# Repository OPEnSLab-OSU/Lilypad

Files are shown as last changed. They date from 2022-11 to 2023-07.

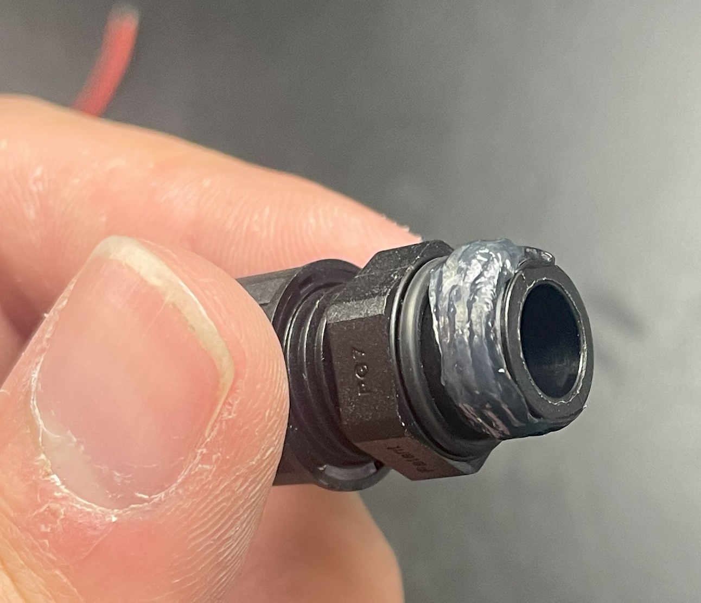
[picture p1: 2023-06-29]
Documentation/images/ElectronicsBoxAssembly/IMG_1301.jpg

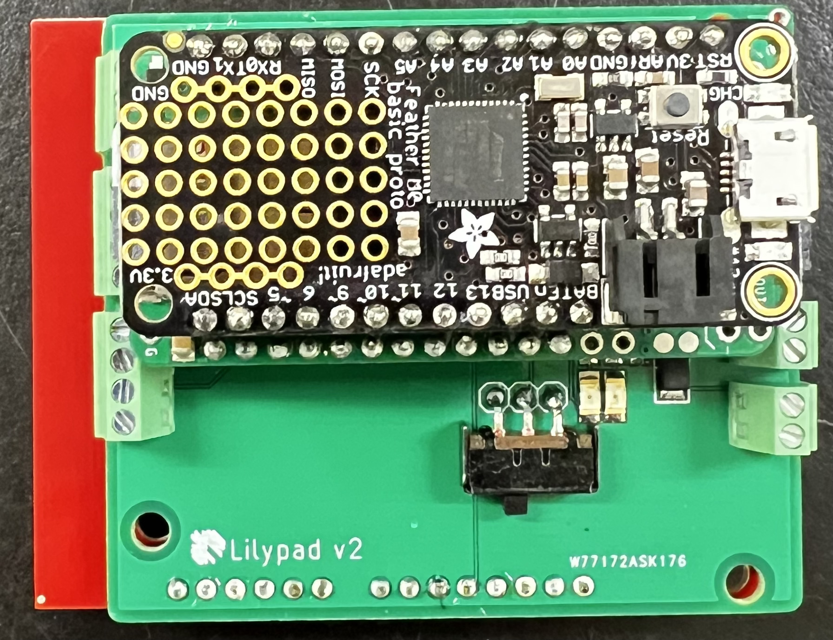
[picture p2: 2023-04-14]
Documentation/images/Hardware/stackup.jpg

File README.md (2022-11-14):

# Lilypad | [Wiki](https://github.com/OPEnSLab-OSU/Lilypad/wiki)
Project Lead: **Colin Hale-Brown**
Project Members: **Cameron Whitlow**, **Aiden Olsen**

Interested in the project? Email us at: halebroc@oregonstate.edu

The Lilypad is a floating water monitoring solution. It is able to measure water temperature, air temperature, humidity, and solar energy per square meter. It is designed to be easy to transport and deployed for at least 1 year at a time.

More information about assembly, testing, and operation can be found at the [wiki](https://github.com/OPEnSLab-OSU/Lilypad/wiki).

Ensure the 4G board has its switched in the Hardware and Shield orientations.

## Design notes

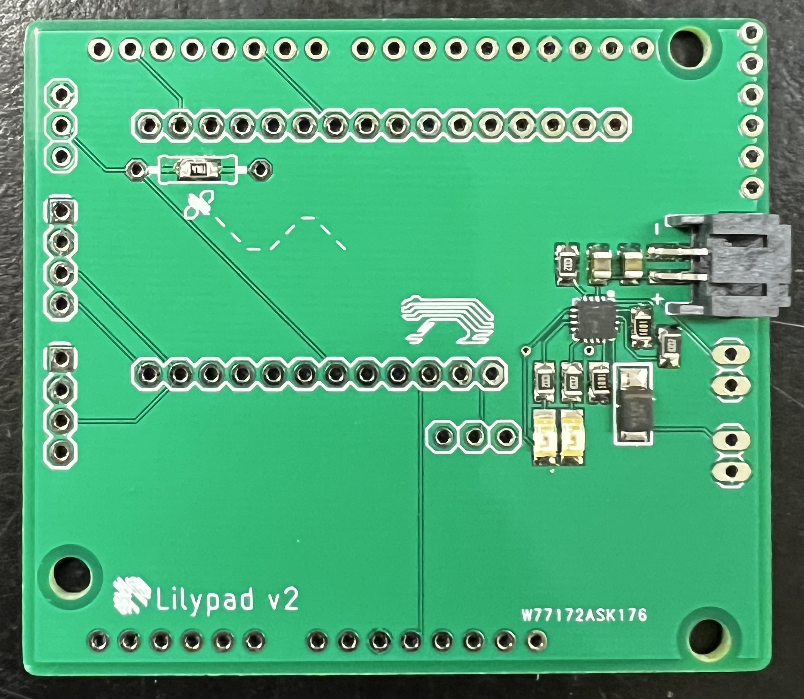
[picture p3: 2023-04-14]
Documentation/images/Hardware/pcb_smd.jpg

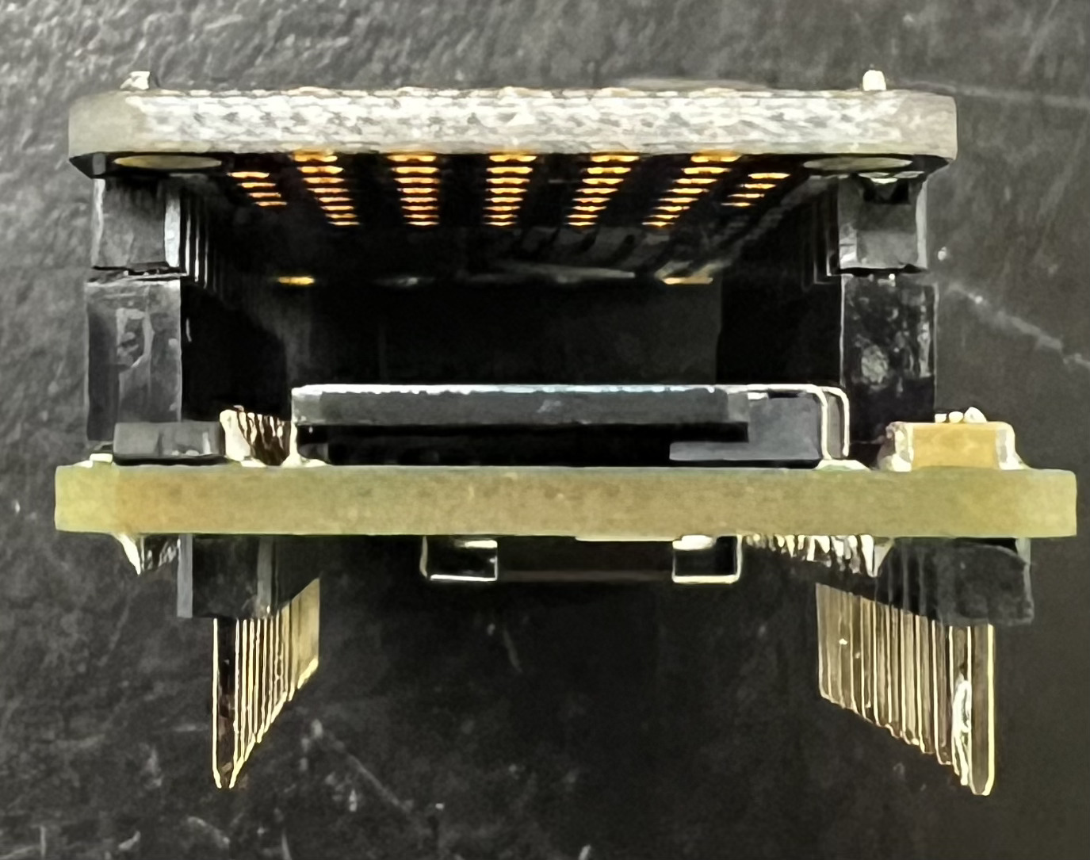
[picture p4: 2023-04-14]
Documentation/images/Hardware/hypnos_feather_back.jpg

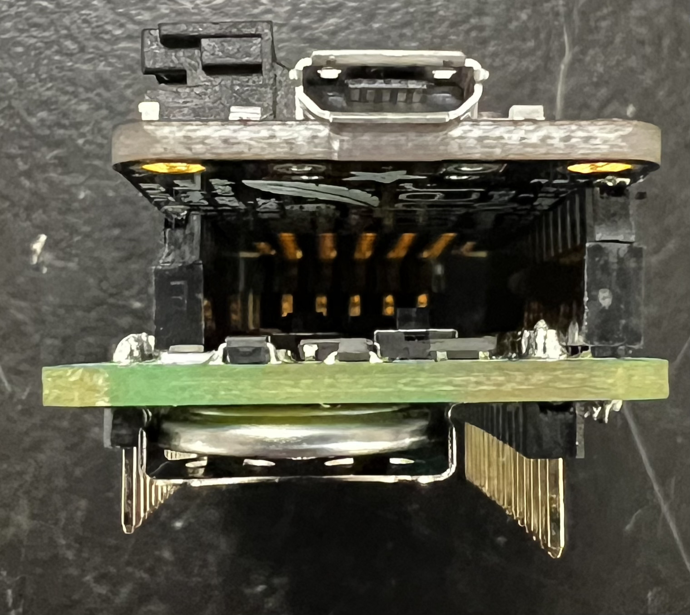
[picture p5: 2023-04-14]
Documentation/images/Hardware/hypnos_feather_front.jpg

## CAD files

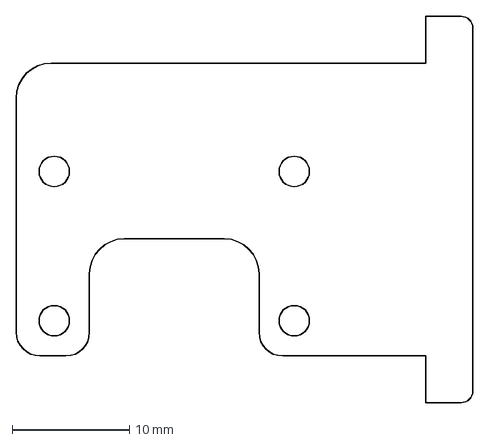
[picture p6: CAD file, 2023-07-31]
CAD/LP_VEML_Mount v4.dxf
39.0 x 33.0 mm

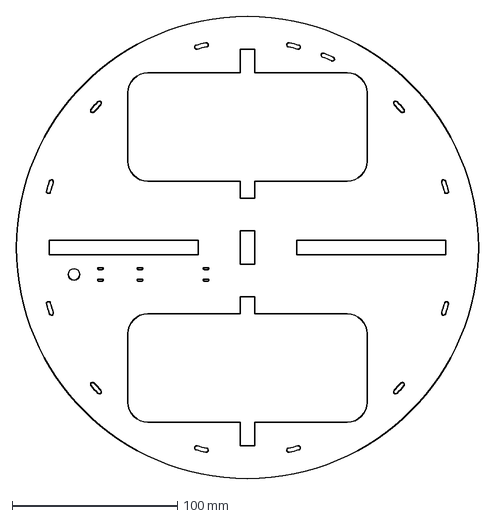
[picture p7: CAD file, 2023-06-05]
CAD/LP_Raft-v1.dxf
280.0 x 280.0 mm

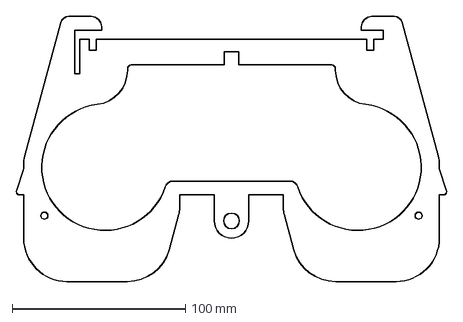
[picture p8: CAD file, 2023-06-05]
CAD/LP_StructurePanel_B-v2.dxf
248.7 x 153.0 mm

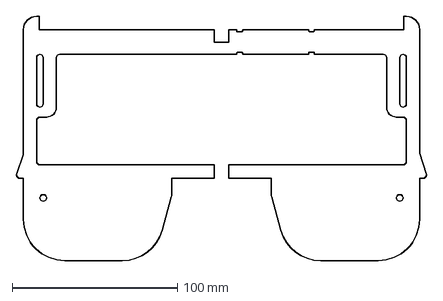
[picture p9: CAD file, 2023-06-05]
CAD/LP_StructurePanel_A-v1.dxf
248.7 x 148.0 mm

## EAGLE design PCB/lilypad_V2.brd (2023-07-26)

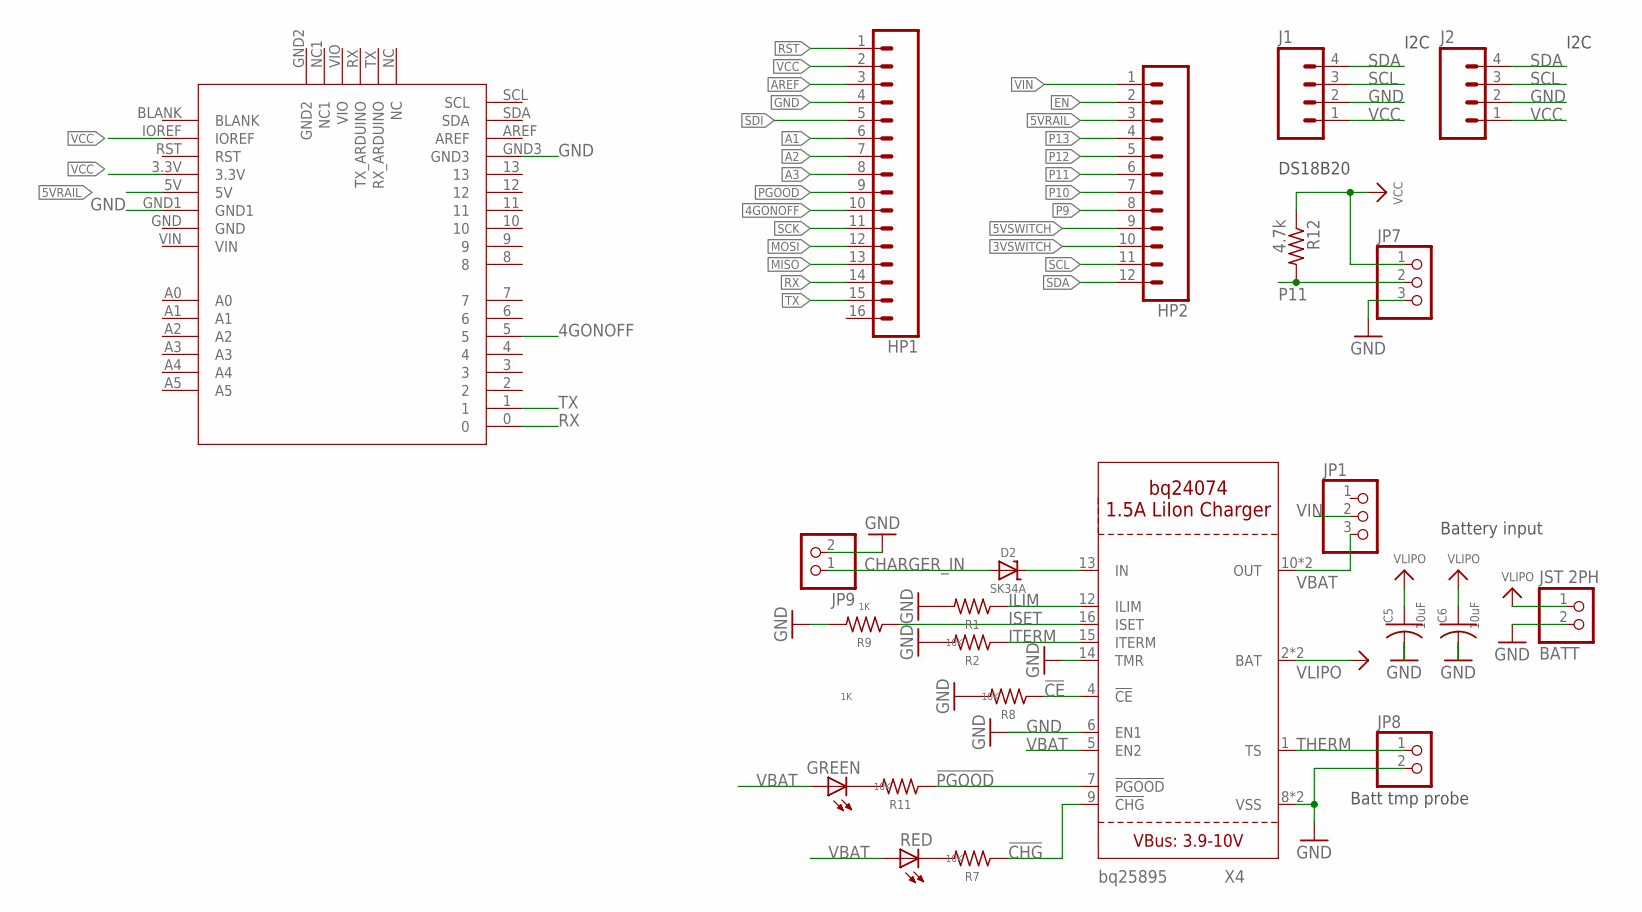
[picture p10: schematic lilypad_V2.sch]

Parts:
BATT: JST 2PH; JST-PH-2-SMT-RA
C5, C6: 10uF; C0805K
D2: SK34A; SMADIODE
GREEN: LEDSMT1206; 1206
HP1: CONN_16; 1X16
HP2: CONN_12; 1X12
J1, J2: M04PTH; 1X04
JP1, JP7: PINHD-1X3; 1X03
JP8, JP9: PINHD-1X2; 1X02
R1, R9: 1K; M0805
R2, R7, R8, R11: 10K; M0805
R12: 4.7k; 0805-THM
RED: LEDSMT1206; 1206
U$2: LTE_BOARD; LTE_BOARD_FOOTPRINT
X4: BQ24074; QFN16_3MM

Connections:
3VSWITCH: HP2.10
4GONOFF: HP1.10, U$2.5
5VRAIL: HP2.3, U$2.5V
5VSWITCH: HP2.9
!CE: R8.1, X4.4 (!CE)
!CHG: R7.1, X4.9 (!CHG)
!PGOOD: R11.1, X4.7 (!PGOOD)
A1: HP1.6
A2: HP1.7
A3: HP1.8
AREF: HP1.3
CHARGER_IN: D2.A, JP9.1
EN: HP2.2
GND: BATT.2 (1), C5.2, C6.2, HP1.4, J1.2, J2.2, JP7.3, JP8.2, JP9.2, R1.2, R2.2, R8.2, R9.2, U$2.GND1, U$2.GND3, X4.6 (EN1), X4.8 (VSS), X4.14 (TMR), X4.THERMAL (VSS)
ILIM: R1.1, X4.12 (ILIM)
ISET: R9.1, X4.16 (ISET)
ITERM: R2.1, X4.15 (ITERM)
MISO: HP1.13
MOSI: HP1.12
unnamed: GREEN.C, R11.2
unnamed: D2.C, X4.13 (IN)
unnamed: R7.2, RED.C
P9: HP2.8
P10: HP2.7
P11: HP2.6, JP7.2, R12.2
P12: HP2.5
P13: HP2.4
PGOOD: HP1.9
RST: HP1.1
RX: HP1.14, U$2.0
SCK: HP1.11
SCL: HP2.11, J1.3, J2.3
SDA: HP2.12, J1.4, J2.4
SDI: HP1.5
THERM: JP8.1, X4.1 (TS)
TX: HP1.15, U$2.1
VBAT: GREEN.A, JP1.3, RED.A, X4.5 (EN2), X4.10 (OUT), X4.11 (OUT)
VCC: HP1.2, J1.1, J2.1, JP7.1, R12.1, U$2.3.3V, U$2.IOREF
VIN: HP2.1, JP1.2
VLIPO: BATT.1 (2), C5.1, C6.1, X4.2 (BAT), X4.3 (BAT)

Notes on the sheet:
DS18B20
Batt tmp probe
Battery input
I2C

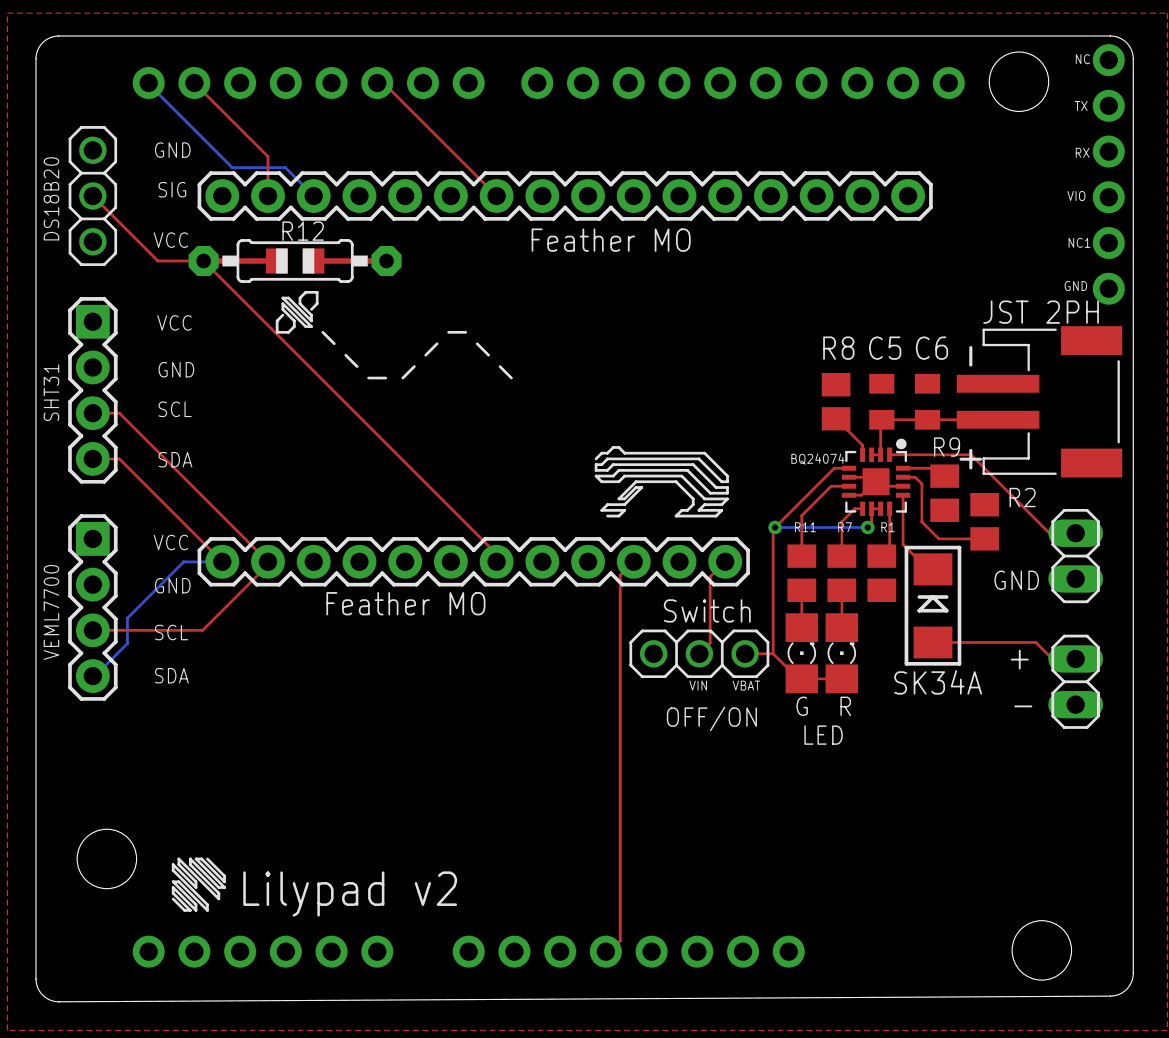
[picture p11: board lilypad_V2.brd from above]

Board: 2 copper layers, 61.0 x 53.7 mm, 26 parts (1 on the bottom side), 23 nets.

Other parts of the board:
H1, H2, H3: STAND-OFF

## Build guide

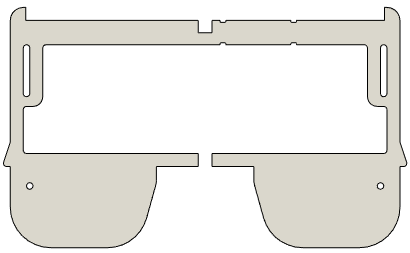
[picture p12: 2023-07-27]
Documentation/images/StructureAssembly/StructurePanelA_rendering.png

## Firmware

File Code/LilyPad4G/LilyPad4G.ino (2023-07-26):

/**
 * LilyPad4G.ino
 * 
 * This project (https://github.com/OPEnSLab-OSU/Lilypad) uses the VEML7700, DS18B20, and SHT31 sensors to log environment data and logs it to both the SD card and also MQTT/MongoDB
 * Required Packages: Altered VEML7700, OneWire, DallasTemperature, Loom4 commit 63b8fd5 or later
 */

// COMMENT THE FOLLOWING LINE TO NOT USE INTERNET
#define USE_INTERNET
// COMMENT THE FOLLOWING LINE TO NOT USE RTC INTERRUPT
#define USE_RTC_INT
#define INT_MIN 2      // Sets sleep time in minutes when RTC is used
#define DEBUG_DELAY 2  // Sets delay time in seconds when rtc interrupt isnt used

#define COLLECTION_NAME "LP1"

#include "arduino_secrets.h"

// Loom includes
#include <Loom_Manager.h>
#include <Hardware/Loom_Hypnos/Loom_Hypnos.h>
#include <Logger.h>
// Sensor Includes
#include <Sensors/Loom_Analog/Loom_Analog.h>
#include <Sensors/I2C/Loom_SHT31/Loom_SHT31.h>
// Internet/DB Includes
#ifdef USE_INTERNET
#include <Internet/Logging/Loom_MQTT/Loom_MQTT.h>
#include <Internet/Connectivity/Loom_LTE/Loom_LTE.h>
#endif
// OneWire Includes
#include <OneWire.h>
#include <DallasTemperature.h>
// Adafruit VEML7700 breakout include
#include "Adafruit_VEML7700.h"

Manager manager(COLLECTION_NAME, 1);                                      //Establish the Loom manager first
Loom_Hypnos hypnos(manager, HYPNOS_VERSION::V3_2, TIME_ZONE::PST, true);  // Create a new Hypnos object
Loom_Analog analog(manager);                                              // Add battery voltage measurement

// Create sensor classes
Loom_SHT31 sht(manager);
// Create lte and mqtt classes
#ifdef USE_INTERNET
Loom_LTE lte(manager, NETWORK_APN, NETWORK_USER, NETWORK_PASS);
Loom_MQTT mqtt(manager, lte.getClient(), SECRET_BROKER, SECRET_PORT, DATABASE, BROKER_USER, BROKER_PASS, "LilyPad");
#endif

// Create oneWire/DallasTemperature sensor classes
#define ONE_WIRE_BUS 11
OneWire oneWire(ONE_WIRE_BUS);
DallasTemperature sensors(&oneWire);
DeviceAddress ds18b20Address;

// Initialize Adafruit VEML7700 class
Adafruit_VEML7700 veml = Adafruit_VEML7700();

// Called when the RTC interrupt is triggered
void isrTrigger() {
  hypnos.wakeup();
}

void setup() {
  ENABLE_SD_LOGGING;
  ENABLE_FUNC_SUMMARIES;
  manager.beginSerial();                 // Wait 20 seconds for the serial console to open
  hypnos.enable();                       // Enable the hypnos rails
  manager.initialize();                  // Initialize all in-use modules
  hypnos.registerInterrupt(isrTrigger);  // Register the ISR and attach to the interrupt
  sensors.begin();                       // locate onewire devices on the bus
  Serial.printf("[OneWire] Found %d devides...\n", sensors.getDeviceCount());
  if (sensors.getDeviceCount() == 0) {
    while (1) { Serial.println("[DS18B20] Sensor not found..."); }
  }
  if (!sensors.getAddress(ds18b20Address, 0)) Serial.println("[DS18B20] Unable to find address for Device 0");
  Serial.printf("[DS18B20] Address: 0x%x...\n", ds18b20Address);
  sensors.setResolution(ds18b20Address, 12);  // Set to the highest resolution
  Serial.printf("[DS18B20] Resolution: %d...\n", sensors.getResolution(ds18b20Address));
  Wire.begin();
  if (!veml.begin()) {  // Startup veml sensor communication and set defaults
    while (1) { Serial.println("[VEML7700] Sensor not found..."); }
  } else {
    Serial.println("[VEML7700] Sensor found...");
  }
}

void loop() {
  sensors.requestTemperatures();                   // Send the command to get temperatures
  float tempC = sensors.getTempC(ds18b20Address);  // Extract the temperature in C
  veml.begin();
  float autoLux = veml.readLux(VEML_LUX_AUTO);
  uint16_t rawALS = veml.readALS();
  uint16_t rawWhite = veml.readWhite();
  manager.measure();                                   // Measure sensor values
  manager.package();                                   // Package data from measurments
  manager.addData("DS18B20", "Temperature", tempC);    // Manually add the data to the JSON
  manager.addData("VEML7700", "Raw_ALS", rawALS);      // Manually add raw ALS value
  manager.addData("VEML7700", "Raw_White", rawWhite);  //Manually add raw White value
  manager.addData("VEML7700", "LUX", autoLux);         // Manually add auto LUX value
  manager.display_data();                              // Print the current JSON packet
  hypnos.logToSD();
  veml.end();  // Log the data to the SD card
#ifdef USE_INTERNET
  mqtt.publish();  // Publish the collected data to MQTT
#endif
#ifdef USE_RTC_INT
  hypnos.setInterruptDuration(TimeSpan(0, 0, INT_MIN, 0));  // Interrupt
  hypnos.reattachRTCInterrupt();
  hypnos.sleep();
#else
  delay(DEBUG_DELAY * 1000);
#endif
}

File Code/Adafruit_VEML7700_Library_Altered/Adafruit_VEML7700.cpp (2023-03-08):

/*!
 *  @file Adafruit_VEML7700.cpp
 *
 *  @mainpage Adafruit VEML7700 I2C Lux Sensor
 *
 *  @section intro_sec Introduction
 *
 * 	I2C Driver for the VEML7700 I2C Lux sensor
 *
 * 	This is a library for the Adafruit VEML7700 breakout:
 * 	http://www.adafruit.com/
 *
 * 	Adafruit invests time and resources providing this open source code,
 *  please support Adafruit and open-source hardware by purchasing products from
 * 	Adafruit!
 *
 *  @section author Author
 *
 *  Limor Fried (Adafruit Industries)
 *
 * 	@section license License
 *
 * 	BSD (see license.txt)
 *
 * 	@section  HISTORY
 *
 *     v1.0 - First release
 */

#include "Adafruit_VEML7700.h"

/*!
 *    @brief  Instantiates a new VEML7700 class
 */
Adafruit_VEML7700::Adafruit_VEML7700(void) {}

/*!
 *    @brief  Sets up the hardware for talking to the VEML7700
 *    @param  theWire An optional pointer to an I2C interface
 *    @return True if initialization was successful, otherwise false.
 */
bool Adafruit_VEML7700::begin(TwoWire *theWire) {
  
  i2c_dev = new Adafruit_I2CDevice(VEML7700_I2CADDR_DEFAULT, theWire);

  if (!i2c_dev->begin()) {
    return false;
  }

  ALS_Config =
      new Adafruit_I2CRegister(i2c_dev, VEML7700_ALS_CONFIG, 2, LSBFIRST);
  ALS_HighThreshold = new Adafruit_I2CRegister(
      i2c_dev, VEML7700_ALS_THREHOLD_HIGH, 2, LSBFIRST);
  ALS_LowThreshold =
      new Adafruit_I2CRegister(i2c_dev, VEML7700_ALS_THREHOLD_LOW, 2, LSBFIRST);
  Power_Saving =
      new Adafruit_I2CRegister(i2c_dev, VEML7700_ALS_POWER_SAVE, 2, LSBFIRST);
  ALS_Data = new Adafruit_I2CRegister(i2c_dev, VEML7700_ALS_DATA, 2, LSBFIRST);
  White_Data =
      new Adafruit_I2CRegister(i2c_dev, VEML7700_WHITE_DATA, 2, LSBFIRST);
  Interrupt_Status =
      new Adafruit_I2CRegister(i2c_dev, VEML7700_INTERRUPTSTATUS, 2, LSBFIRST);

  ALS_Shutdown =
      new Adafruit_I2CRegisterBits(ALS_Config, 1, 0); // # bits, bit_shift
  ALS_Interrupt_Enable = new Adafruit_I2CRegisterBits(ALS_Config, 1, 1);
  ALS_Persistence = new Adafruit_I2CRegisterBits(ALS_Config, 2, 4);
  ALS_Integration_Time = new Adafruit_I2CRegisterBits(ALS_Config, 4, 6);
  ALS_Gain = new Adafruit_I2CRegisterBits(ALS_Config, 2, 11);
  PowerSave_Enable = new Adafruit_I2CRegisterBits(Power_Saving, 1, 0);
  PowerSave_Mode = new Adafruit_I2CRegisterBits(Power_Saving, 2, 1);

  enable(false);
  interruptEnable(false);
  setPersistence(VEML7700_PERS_1);
  setGain(VEML7700_GAIN_1_8);
  setIntegrationTime(VEML7700_IT_100MS);
  powerSaveEnable(false);
  enable(true);

  lastRead = millis();

  return true;
}

void Adafruit_VEML7700::end(void) {
  delete i2c_dev;
  delete ALS_Config;
  delete ALS_HighThreshold;
  delete ALS_LowThreshold;
  delete Power_Saving;
  delete ALS_Data;
  delete White_Data;
  delete Interrupt_Status;
  delete ALS_Shutdown;
  delete ALS_Interrupt_Enable;
  delete ALS_Persistence;
  delete ALS_Integration_Time;
  delete ALS_Gain;
  delete PowerSave_Enable;
  delete PowerSave_Mode;
}

/*!
 *    @brief Read the calibrated lux value. See app note lux table on page 5
 *    @param method Lux comptation method to use. One of
 *    @returns Floating point Lux data
 */
float Adafruit_VEML7700::readLux(luxMethod method) {
  bool wait = true;

  if (method == VEML_LUX_NORMAL_NOWAIT || method == VEML_LUX_CORRECTED_NOWAIT)
    wait = false;

  switch (method) {
  case VEML_LUX_NORMAL:
    return computeLux(readALS(wait));
  case VEML_LUX_CORRECTED:
    return computeLux(readALS(wait), true);
  case VEML_LUX_AUTO:
    return autoLux();
  default:
    return -1;
  }
}

/*!
 *    @brief Read the raw ALS data
 *    @param wait If false (default), read out measurement with no delay. If
 * true, wait as need based on integration time before reading out measurement
 * results.
 *    @returns 16-bit data value from the ALS register
 */
uint16_t Adafruit_VEML7700::readALS(bool wait) {
  if (wait)
    readWait();
  lastRead = millis();
  return ALS_Data->read();
}

/*!
 *    @brief Read the raw white light data
 *    @param wait If false (default), read out measurement with no delay. If
 * true, wait as need based on integration time before reading out measurement
 * results.
 *    @returns 16-bit data value from the WHITE register
 */
uint16_t Adafruit_VEML7700::readWhite(bool wait) {
  if (wait)
    readWait();
  lastRead = millis();
  return White_Data->read();
}

/*!
 *    @brief Enable or disable the sensor
 *    @param enable The flag to enable/disable
 */
void Adafruit_VEML7700::enable(bool enable) {
  ALS_Shutdown->write(!enable);
  // From app note:
  //   '''
  //   When activating the sensor, set bit 0 of the command register
  //   to “0” with a wait time of 2.5 ms before the first measurement
  //   is needed, allowing for the correct start of the signal
  //   processor and oscillator.
  //   '''
  if (enable)
    delay(5); // doubling 2.5ms spec to be sure
}

/*!
 *    @brief Ask if the interrupt is enabled
 *    @returns True if enabled, false otherwise
 */
bool Adafruit_VEML7700::enabled(void) { return !ALS_Shutdown->read(); }

/*!
 *    @brief Enable or disable the interrupt
 *    @param enable The flag to enable/disable
 */
void Adafruit_VEML7700::interruptEnable(bool enable) {
  ALS_Interrupt_Enable->write(enable);
}

/*!
 *    @brief Ask if the interrupt is enabled
 *    @returns True if enabled, false otherwise
 */
bool Adafruit_VEML7700::interruptEnabled(void) {
  return ALS_Interrupt_Enable->read();
}

/*!
 *    @brief Set the ALS IRQ persistance setting
 *    @param pers Persistance constant, can be VEML7700_PERS_1, VEML7700_PERS_2,
 *    VEML7700_PERS_4 or VEML7700_PERS_8
 */
void Adafruit_VEML7700::setPersistence(uint8_t pers) {
  ALS_Persistence->write(pers);
}

/*!
 *    @brief Get the ALS IRQ persistance setting
 *    @returns Persistance constant, can be VEML7700_PERS_1, VEML7700_PERS_2,
 *    VEML7700_PERS_4 or VEML7700_PERS_8
 */
uint8_t Adafruit_VEML7700::getPersistence(void) {
  return ALS_Persistence->read();
}

/*!
 *    @brief Set ALS integration time
 *    @param it Can be VEML7700_IT_100MS, VEML7700_IT_200MS, VEML7700_IT_400MS,
 *    VEML7700_IT_800MS, VEML7700_IT_50MS or VEML7700_IT_25MS
 *    @param wait Waits to insure old integration time cycle has completed. This
 * is a blocking delay. If disabled by passing false, user code must insure a
 * new reading is not done before old integration cycle completes.
 */
void Adafruit_VEML7700::setIntegrationTime(uint8_t it, bool wait) {
  // save current integration time
  int flushDelay = wait ? getIntegrationTimeValue() : 0;
  // set new integration time
  ALS_Integration_Time->write(it);
  // pause old integration time to insure sensor cycle has completed
  delay(flushDelay);
  // reset counter
  lastRead = millis();
}

/*!
 *    @brief Get ALS integration time setting
 *    @returns IT index, can be VEML7700_IT_100MS, VEML7700_IT_200MS,
 * VEML7700_IT_400MS, VEML7700_IT_800MS, VEML7700_IT_50MS or VEML7700_IT_25MS
 */
uint8_t Adafruit_VEML7700::getIntegrationTime(void) {
  return ALS_Integration_Time->read();
}

/*!
 *    @brief Get ALS integration time value
 *    @returns ALS integration time in milliseconds
 */
int Adafruit_VEML7700::getIntegrationTimeValue(void) {
  switch (getIntegrationTime()) {
  case VEML7700_IT_25MS:
    return 25;
  case VEML7700_IT_50MS:
    return 50;
  case VEML7700_IT_100MS:
    return 100;
  case VEML7700_IT_200MS:
    return 200;
  case VEML7700_IT_400MS:
    return 400;
  case VEML7700_IT_800MS:
    return 800;
  default:
    return -1;
  }
}

/*!
 *    @brief Set ALS gain
 *    @param gain Can be VEML7700_GAIN_1, VEML7700_GAIN_2, VEML7700_GAIN_1_8 or
 * VEML7700_GAIN_1_4
 */
void Adafruit_VEML7700::setGain(uint8_t gain) {
  ALS_Gain->write(gain);
  lastRead = millis(); // reset
}

/*!
 *    @brief Get ALS gain setting
 *    @returns Gain index, can be VEML7700_GAIN_1, VEML7700_GAIN_2,
 * VEML7700_GAIN_1_8 or VEML7700_GAIN_1_4
 */
uint8_t Adafruit_VEML7700::getGain(void) { return ALS_Gain->read(); }

/*!
 *    @brief Get ALS gain value
 *    @returns Actual gain value as float
 */
float Adafruit_VEML7700::getGainValue(void) {
  switch (getGain()) {
  case VEML7700_GAIN_1_8:
    return 0.125;
  case VEML7700_GAIN_1_4:
    return 0.25;
  case VEML7700_GAIN_1:
    return 1;
  case VEML7700_GAIN_2:
    return 2;
  default:
    return -1;
  }
}

/*!
 *    @brief Enable power save mode
 *    @param enable True if power save should be enabled
 */
void Adafruit_VEML7700::powerSaveEnable(bool enable) {
  PowerSave_Enable->write(enable);
}

/*!
 *    @brief Check if power save mode is enabled
 *    @returns True if power save is enabled
 */
bool Adafruit_VEML7700::powerSaveEnabled(void) {
  return PowerSave_Enable->read();
}

/*!
 *    @brief Assign the power save register data
 *    @param mode The 16-bit data to write to VEML7700_ALS_POWER_SAVE
 */
void Adafruit_VEML7700::setPowerSaveMode(uint8_t mode) {
  PowerSave_Mode->write(mode);
}

/*!
 *    @brief  Retrieve the power save register data
 *    @return 16-bit data from VEML7700_ALS_POWER_SAVE
 */
uint8_t Adafruit_VEML7700::getPowerSaveMode(void) {
  return PowerSave_Mode->read();
}

/*!
 *    @brief Assign the low threshold register data
 *    @param value The 16-bit data to write to VEML7700_ALS_THREHOLD_LOW
 */
void Adafruit_VEML7700::setLowThreshold(uint16_t value) {
  ALS_LowThreshold->write(value);
}

/*!
 *    @brief  Retrieve the low threshold register data
 *    @return 16-bit data from VEML7700_ALS_THREHOLD_LOW
 */
uint16_t Adafruit_VEML7700::getLowThreshold(void) {
  return ALS_LowThreshold->read();
}

/*!
 *    @brief Assign the high threshold register data
 *    @param value The 16-bit data to write to VEML7700_ALS_THREHOLD_HIGH
 */
void Adafruit_VEML7700::setHighThreshold(uint16_t value) {
  ALS_HighThreshold->write(value);
}

/*!
 *    @brief  Retrieve the high threshold register data
 *    @return 16-bit data from VEML7700_ALS_THREHOLD_HIGH
 */
uint16_t Adafruit_VEML7700::getHighThreshold(void) {
  return ALS_HighThreshold->read();
}

/*!
 *    @brief  Retrieve the interrupt status register data
 *    @return 16-bit data from VEML7700_INTERRUPTSTATUS
 */
uint16_t Adafruit_VEML7700::interruptStatus(void) {
  return Interrupt_Status->read();
}
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

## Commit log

2022-10-20 Lilypad_V2 PCB First Revision
    [lilypad_V2.brd, lilypad_V2.sch]
2022-10-20 Fixed some sch errors
    [lilypad_V2.brd, lilypad_V2.sch]
2022-10-20 Lilypad PCB Post Review and README
    [lilypad_V2.brd, lilypad_V2.sch]
2022-10-31 Updated shem/pcb w/ correct INA169 footprint
2022-12-05 Update LilyPad4G.ino
    update to work with new temp sensor
2023-01-12 update board schematic
    [lilypad_V2.brd, lilypad_V2.sch]
2023-01-12 Update PCB
    Changed the wire connection type, adjusted for clearance. Fixed GND plane and moved the digital temp. sensor pin to 11.
    [lilypad_V2.brd]
2023-04-14 added assembly pics
2023-04-27 Github Organized for HardwareX and Delivery
    [Evaporometer_ConceptContainer v11.stl]
2023-06-02 pelican case assembly pics
2023-07-26 Added labeled to pcb
    [lilypad_V2.brd]
2023-07-26 Updated labels
    [lilypad_V2.brd]
2023-07-27 Create LP_VEML_Mount v4.dxf
    [LP_VEML_Mount v4.dxf]
2023-07-27 Added gerber file, template arduino secrets
    [Evaporometer_ConceptContainer v11.stl, lilypad_V2.brd, lilypad_V2.sch]
2023-07-28 Replaced VEML mount with final
    [LP_VEML_Mount v4.dxf, LP_VEML_Mount-v1.dxf]
2023-07-31 Update LP_VEML_Mount v4.dxf
    [LP_VEML_Mount v4.dxf]

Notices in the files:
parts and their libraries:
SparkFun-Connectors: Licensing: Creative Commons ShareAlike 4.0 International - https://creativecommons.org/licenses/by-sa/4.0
